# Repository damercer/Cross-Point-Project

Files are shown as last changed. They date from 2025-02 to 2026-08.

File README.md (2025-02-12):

# Cross Point Project
Software-Configured Breadboard Hardware Targeting Circuit Wiring Error Reduction in ECE Labs.
#
Abstract:
#
The hardware project aims to examine the effectiveness of software-configured wiring compared to traditional manual wiring of breadboards. While both methods use actual hardware, the software-configured approach automates the connections between components, thereby minimizing wiring errors and setup time. The intent is to investigate the impact of each approach on student comprehension, engagement, and error rates. By comparing these two approaches, the project seeks to determine which method better supports student engagement, educational outcomes and reduces frustration associated with complex circuit construction.
#
Introduction:
#
Hands-on experiential learning is a cornerstone of ECE education, typically relying on manual wiring of circuits on solderless breadboards. Using a traditional solderless breadboard as the means for building electronic circuit lab experiments requires the student, in addition to placing components, to manually insert wires to connect together the component pins according to a schematic diagram. These manual translation steps from schematic to hardware can lead to wiring errors in the experimental setup that can obscure circuit principles. While this manual wiring method offers valuable experience in physical component handling and troubleshooting, the extra time needed for debugging and correcting these errors leads to frustration and loss of precious lab time to investigate the circuit concept in question.

The goal is to evaluate the educational benefits and potential drawbacks of these software-configured hardware systems compared to traditional manual wiring. By doing so, it addresses the need for balancing hands-on skills with error minimization and conceptual understanding in electrical engineering education.
#
Analog switch matrix cross point experiment breadboard.
#
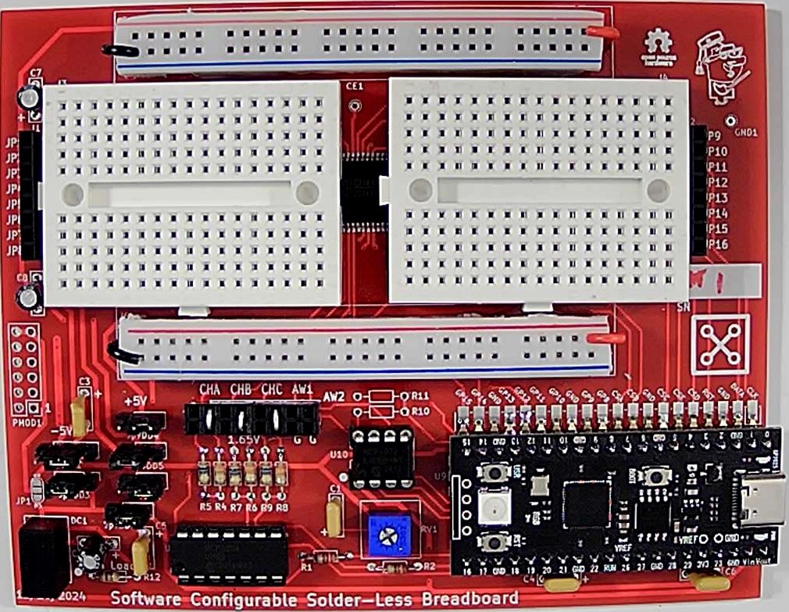
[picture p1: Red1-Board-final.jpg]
Screenshot Prototype PCB

Prototype PCB (Red version)
 
The idea is to computerize the wiring of the breadboard in an effort to reduce student frustration when building complex experiments. Using four analog 16X8 cross point switches wired together into two 32X8 cross points with a fifth switch matrix interconnecting the two smaller arrays into effectively a single 64X16 array.

This breadboard makes real, hardware connections between the 64 breadboard component pins on the board to the16 “jumper” nodes on the board via software commands, instead of needing to manually install jumper wires. The prototype PCB is shown, figure 1, which incorporates two mini 170 pin solderless breadboards, one for each of the 32X8 cross point arrays. There are a combined 68 total component pin locations across both mini breadboards with power distribution strips top and bottom. The two mini breadboards connect to the PCB through pogo pins and so they can be easily removed. It would then be possible to bolt on custom daughter PCBs with whatever components are needed for a given course already installed. Such as CMOS transistor arrays (CD4007) with even some pre-wired sub-circuits like current sources and OTAs.

The combined 64X16 cross point matrix board uses a total of 5 CH446DS 16X8 analog cross point ICs (from China) programed via a RP-2040 micro controller breakout board (Pi Pico or equivalent). Materials cost per board, in quantities of 10 or more, is less than $30 not including the assembly labor.

The board is powered from the Pi Pico USB connection. For powering the experiment circuits, male Pin Jumpers can be set for 0 and +3.3V, 0 and +5V or -5V and +5V power (or 0 and +10V) using an on board isolated 5V DC-DC generator.

LTspice is used to enter the schematic for the experiment. In addition to the standard library symbols a number of supporting schematic library files have been created. Schematic symbols for TO-92 transistors and resistors of various lead spacing are available in the LTspice files.

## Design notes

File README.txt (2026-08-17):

# Cross Point Project
Software-Configured Breadboard Hardware Targeting Circuit Wiring Error Reduction in ECE Labs.
#
Abstract:
#
The hardware project aims to examine the effectiveness of software-configured wiring compared to traditional manual wiring of breadboards. While both methods use actual hardware, the software-configured approach automates the connections between components, thereby minimizing wiring errors and setup time. The intent is to investigate the impact of each approach on student comprehension, engagement, and error rates. By comparing these two approaches, the project seeks to determine which method better supports student engagement, educational outcomes and reduces frustration associated with complex circuit construction.
#
Introduction:
#
Hands-on experiential learning is a cornerstone of ECE education, typically relying on manual wiring of circuits on solderless breadboards. Using a traditional solderless breadboard as the means for building electronic circuit lab experiments requires the student, in addition to placing components, to manually insert wires to connect together the component pins according to a schematic diagram. These manual translation steps from schematic to hardware can lead to wiring errors in the experimental setup that can obscure circuit principles. While this manual wiring method offers valuable experience in physical component handling and troubleshooting, the extra time needed for debugging and correcting these errors leads to frustration and loss of precious lab time to investigate the circuit concept in question.

The goal is to evaluate the educational benefits and potential drawbacks of these software-configured hardware systems compared to traditional manual wiring. By doing so, it addresses the need for balancing hands-on skills with error minimization and conceptual understanding in electrical engineering education.
#
Analog switch matrix cross point experiment breadboard.
#
Screenshot Prototype PCB
Production PCB (Red3 version, instructions for ordering boards can be found in PCB Projects folder)
 
The idea is to computerize the wiring of the breadboard in an effort to reduce student frustration when building complex experiments. Using four analog 16X8 cross point switches wired together into two 32X8 cross points with a fifth switch matrix interconnecting the two smaller arrays into effectively a single 64X16 array.

This breadboard makes real, hardware connections between the 64 breadboard component pins on the board to the 16 “jumper” nodes on the board via software commands, instead of needing to manually install jumper wires. The prototype PCB is shown, figure 1, which incorporates two mini 170 pin solderless breadboards, one for each of the 32X8 cross point arrays. There are a combined 68 total component pin locations across both mini breadboards with power distribution strips top and bottom. The two mini breadboards connect to the PCB through pogo pins and so they can be easily removed. It would then be possible to bolt on custom daughter PCBs with whatever components are needed for a given course already installed. Such as CMOS transistor arrays (CD4007) with even some pre-wired sub-circuits like current sources and OTAs.

The combined 64X16 cross point matrix board uses a total of 5 CH446DS 16X8 analog cross point ICs (from China) programed via a RP-2040 micro controller breakout board (Pi Pico or equivalent). Materials cost per board, in quantities of 10 or more, is less than $30 not including the assembly labor.

The board is powered from the Pi Pico USB connection. For powering the experiment circuits, Jumpers can be configured for 0 and +3.3V, 0 and +5V or -5V and +5V power using an on board isolated 5V DC-DC generator. Pi Pico microcontroller internal 12 bit ADC along with an external dual 12 bit DAC provide some level of data acquisition measurement capability for experiments.

LTspice is used to enter the schematic for the experiment. In addition to the standard library symbols a number of supporting schematic library files have been created. Schematic symbols for TO-92 transistors and resistors of various lead spacing are available in the LTspice files.

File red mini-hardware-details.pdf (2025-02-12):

## Red Mini Hardware Construction (revised 1/20/25):

Analog switch matrix cross point experiment breadboard.

The idea is to computerize the wiring of the breadboard in an effort to reduce student frustration when building complex experiments. Using four analog 16X8 cross point switches wired together into two 32X8 cross points with a fifth switch matrix interconnecting the two smaller arrays into effectively a single 64X16 array.

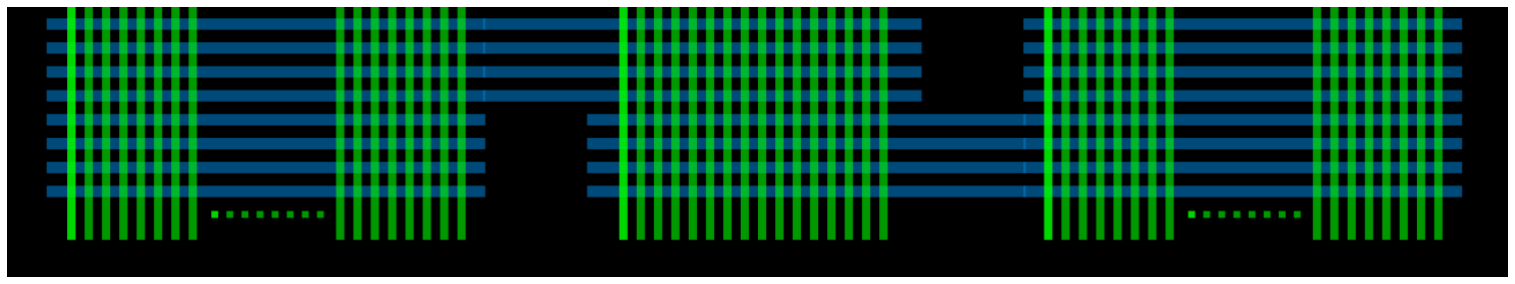
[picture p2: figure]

This breadboard makes real, hardware connections between the 64 breadboard component pins on the board to the16 “jumper” nodes on the board via software commands, instead of needing to manually install jumper wires. The prototype PCB is shown, figure 1, which incorporates two mini 170 pin solderless breadboards, one for each of the 32X8 cross point arrays. There are a combined 68 total component pin locations across both mini breadboards with power distribution strips top and bottom. The two mini breadboards connect to the PCB through pogo pins and so they can be easily removed. It would then be possible to bolt on custom daughter PCBs with whatever components are needed for a given course already installed. Such as CMOS transistor arrays (CD4007) with even some pre-wired sub-circuits like current sources and OTAs.

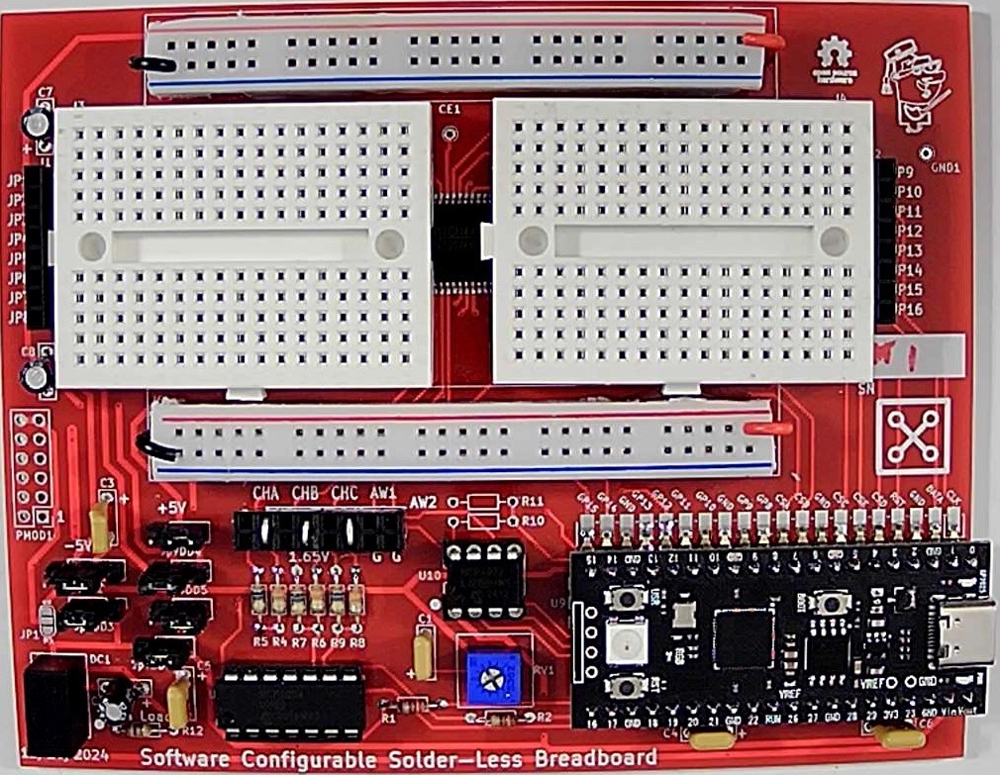
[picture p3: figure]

Figure 1, Prototype PCB.

The combined 64X16 cross point matrix board uses a total of 5 CH446DS [2] 16X8 analog cross point ICs (from China) programed via a RP-2040 micro controller breakout board (Pi Pico[3]
or equivalent).
Materials cost per board, in quantities of 10 or more, is less than $30 not including the assembly labor.

The board is powered from the Pi Pico USB connection. For powering the experiment circuits, male Pin Jumpers can be set for 0 and +3.3V, 0 and +5V or -5V and +5V power (or 0 and +10V) using an on board isolated 5V DC-DC generator.
LTspice[4]
is used to enter the schematic for the experiment. In addition to the standard library symbols a number of supporting schematic library files have been created, figure 2. Schematic symbols for TO-92 transistors and resistors of various lead spacing have been created. There are also example schematic symbols with the proper pin spacing for 8, 14 and 16 pin DIP packages. The standard library components can of course also be used.

The library schematics for the switch matrix connections contain 60 Ω resistors and 16 pF capacitors which model the analog switch. One end of a matrix switch will have the component pin net and the other end will have one of the 16 "jumper" nets (JP1-16).

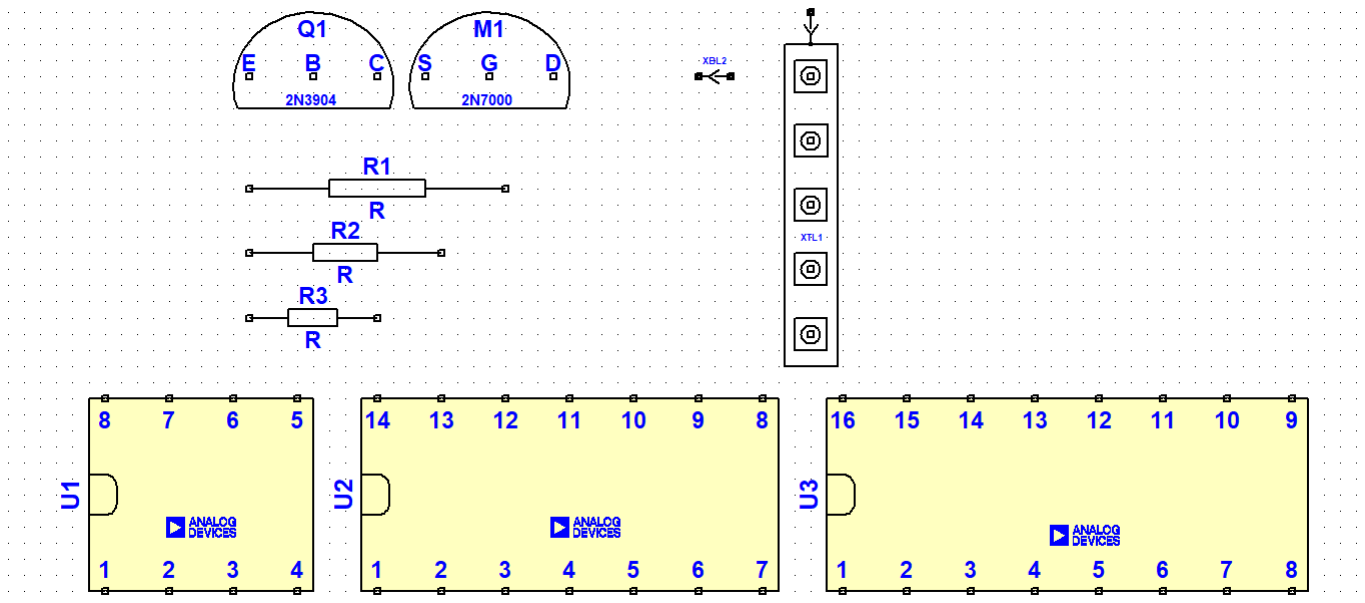
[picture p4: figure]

Figure 2, Schematic symbols.

A floor planning schematic template, figure 3, has been created to help the user figure out where to place the parts on the left and right side mini breadboards and then use the "jumpers" to wire them together. There is a schematic symbol for each breadboard column (the 5 pins shorted together). Each breadboard column has a specific name based on its location. Names are numbered from 1 to 17 starting with the top left section, TL1-17, then the bottom left section, BL1-17, then the top right section TR1-17, and finally the bottom right section, BR1-17.

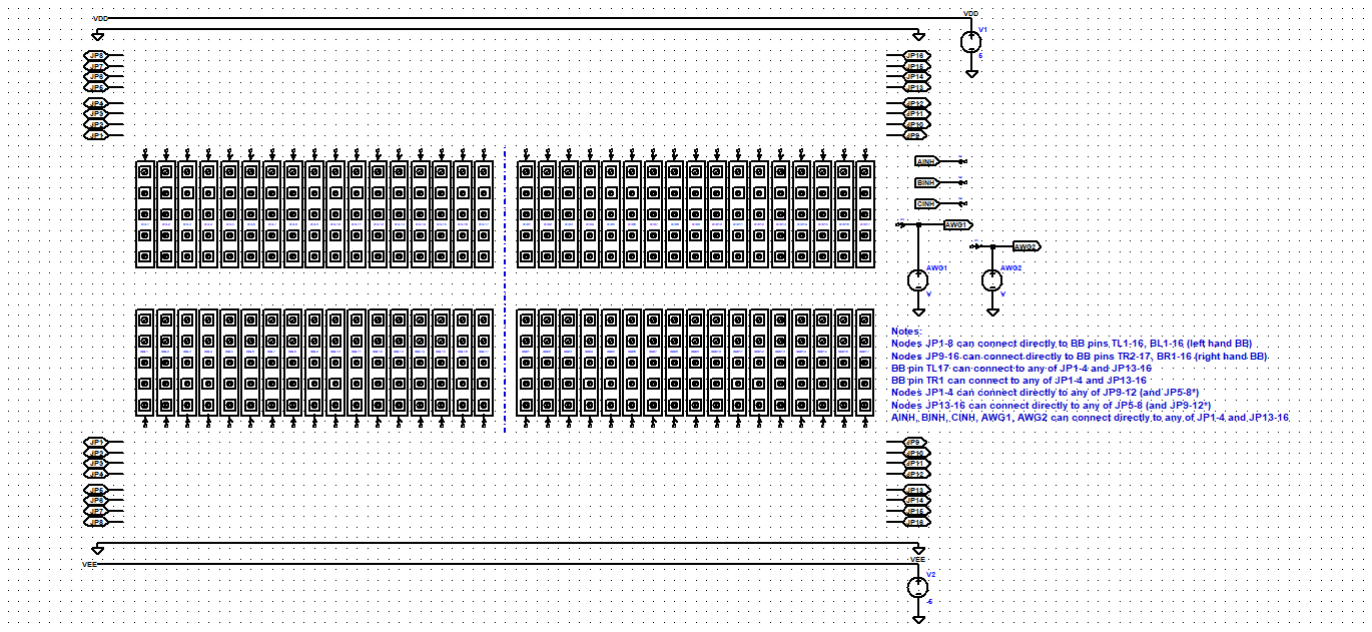
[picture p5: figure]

Figure 3, LTspice floor planner template schematic

In figure 4 we see an example circuit of a transistor level op-amp that has been floorplanned and interconnected with the JP jumper nets. Components can also be connected between a column pin and one of the top and bottom power and ground rails simply by a wire.

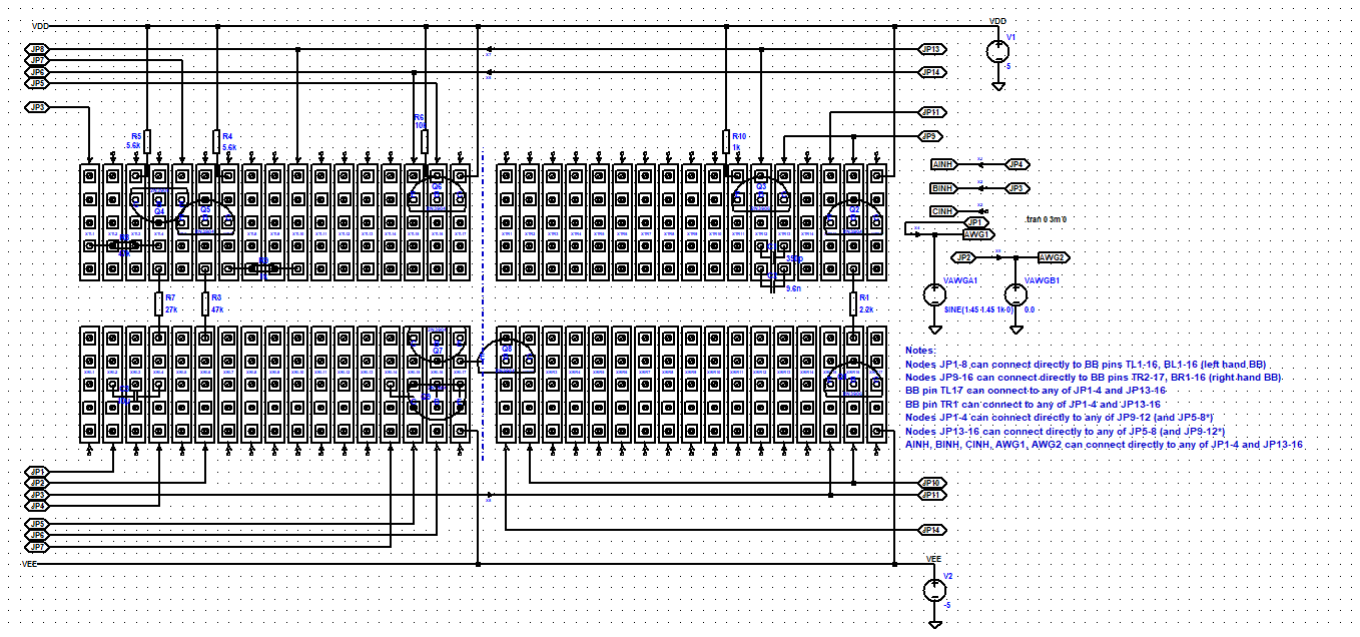
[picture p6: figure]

Figure 4, Example floor planned circuit

There is also a way to draw the circuit as a more conventional schematic, figure 5. The same op-amp circuit has been redrawn using standard symbols from the LTspice library with the addition of single switch interconnection symbols. The little pointy arrow symbols are placed in series with certain nets to indicate the component locations on the breadboard. These interconnection symbols are again named based on the BB holes (TL1-17, BL1-17, TR1-17, BR1-17) the parts are plugged into. This approach is easier to visualize the circuit as a schematic but perhaps harder to floor plan where to place the devices.

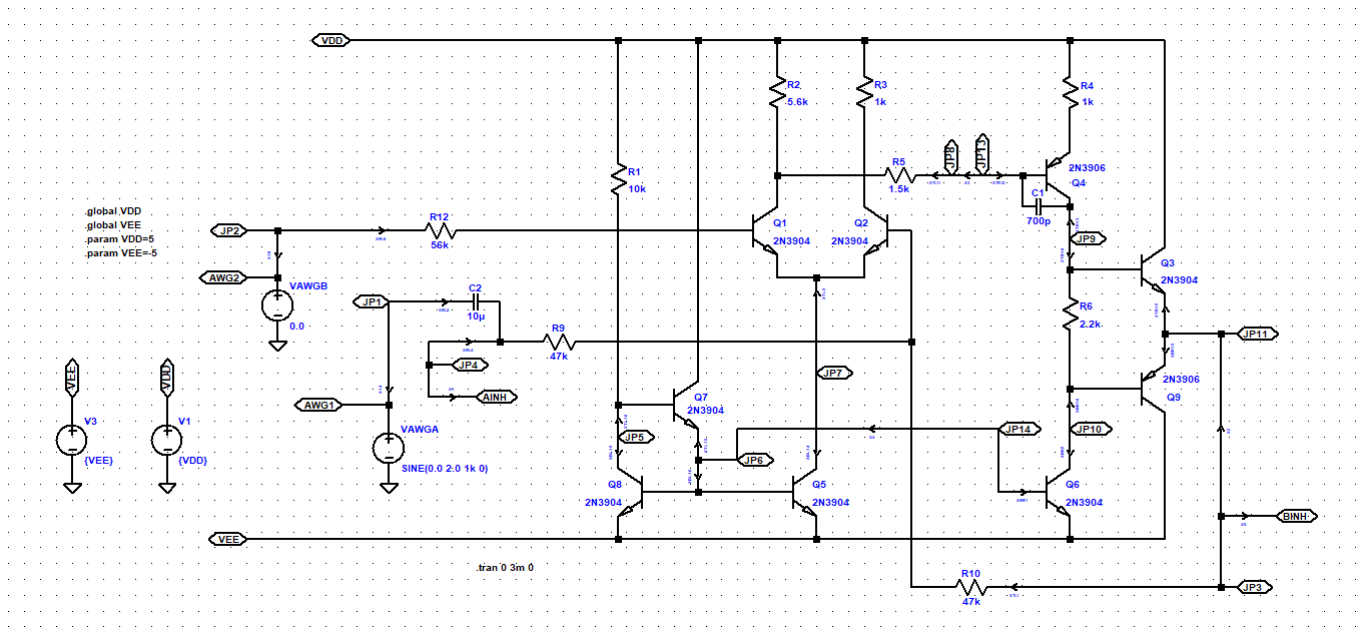
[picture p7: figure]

Figure 5, Conventional Schematic method

Correct simulation results insure that you have it all wired correctly before moving to the actual hardware.

A Python script looks through the saved LTspice .cir net list file looking for sub circuits starting with XX in their names. Then parses the connections based on the names (based on breadboard pin locations, TL1-17, BL1-17, TR1-17, BR1-17) and JP1-16 to send commands to the Pi Pico and on to the cross point switches. Everything else is ignored.

As long as you follow these rules when building the schematic the process is simple and mostly automatic. Programming the board is done through ALICE Universal[5]
using a hardware specific
interface configuration file for this cross point prototype including a way to turn on and off matrix switches manually as well.

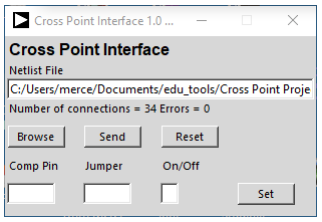
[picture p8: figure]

Cross Point Matrix control user interface The following are a few additional example circuits built using the breadboard.
The LTspice schematic in figure 6 was used to configure four CD4007 transistor arrays as a ring oscillator consisting of 11 CMOS inverter stages. It uses 56 of the 68 possible device pins and all 16 of the jumpers of the switch matrix. Manual jumper wires are used to connect each of the DIP (pins 7 and 14) ground and power pins to the power and ground rails on the board. All other connections are programed by the netlist.

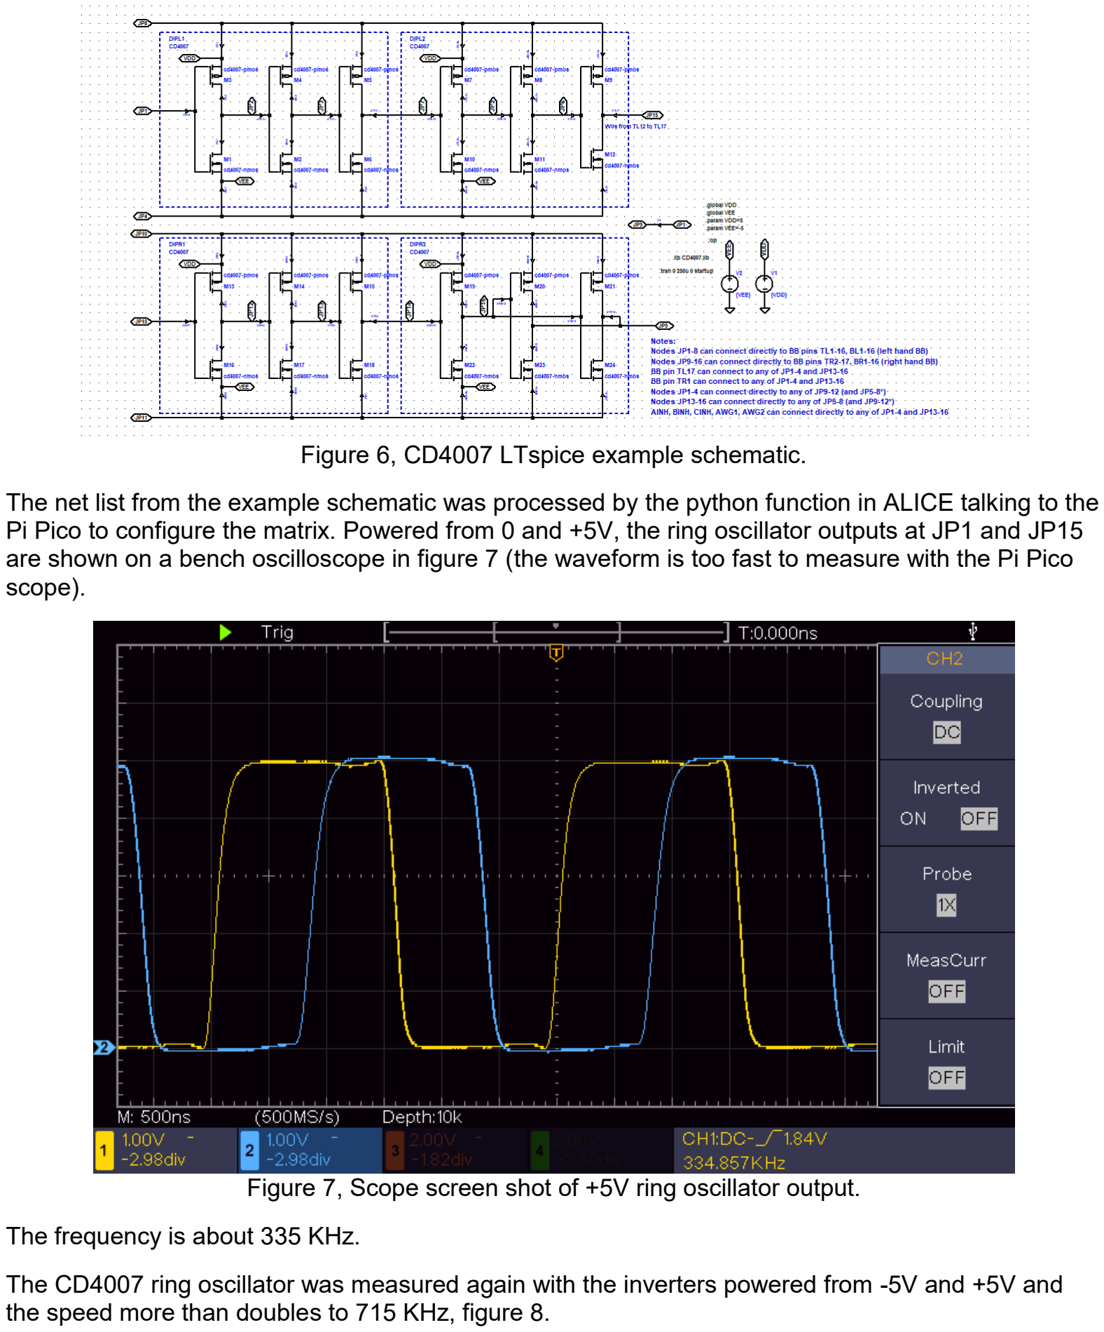
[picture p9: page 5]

Figure 6, CD4007 LTspice example schematic.

The net list from the example schematic was processed by the python function in ALICE talking to the Pi Pico to configure the matrix. Powered from 0 and +5V, the ring oscillator outputs at JP1 and JP15 are shown on a bench oscilloscope in figure 7 (the waveform is too fast to measure with the Pi Pico scope).

Figure 7, Scope screen shot of +5V ring oscillator output.

The frequency is about 335 KHz.

The CD4007 ring oscillator was measured again with the inverters powered from -5V and +5V and the speed more than doubles to 715 KHz, figure 8.

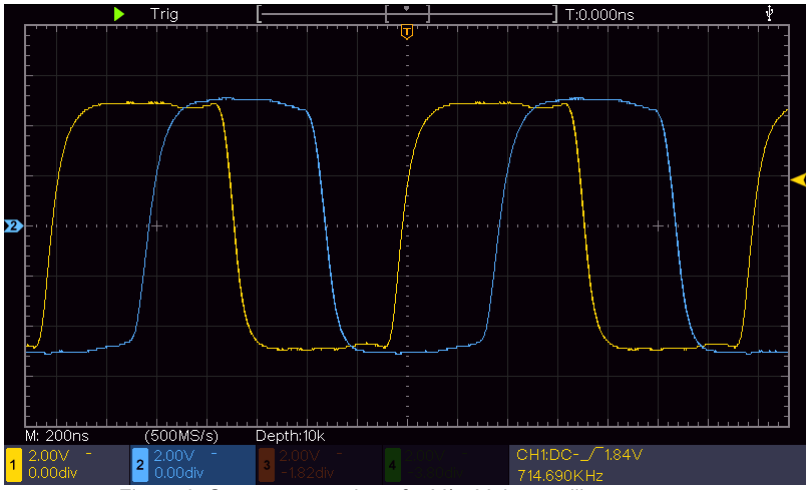
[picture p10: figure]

Figure 8, Scope screen shot of -5V/+5V ring oscillator output.

A Schmitt trigger relaxation oscillator can be constructed from the CD4007 CMOS transistor level inverters, figure 9. The Schmitt trigger is made by rearranging the connections and adding resistor R1 and Capacitor C1 to set the frequency. The M1,3 and M7,10 inverters are stronger than the other 4 inverters because their sources are connected directly to VDD and VEE rather than through the 60 Ω switch resistances. A “strong” inverter and a “weak” inverter are connected as a latch. This latch action determines the high and low threshold of the Schmitt trigger.

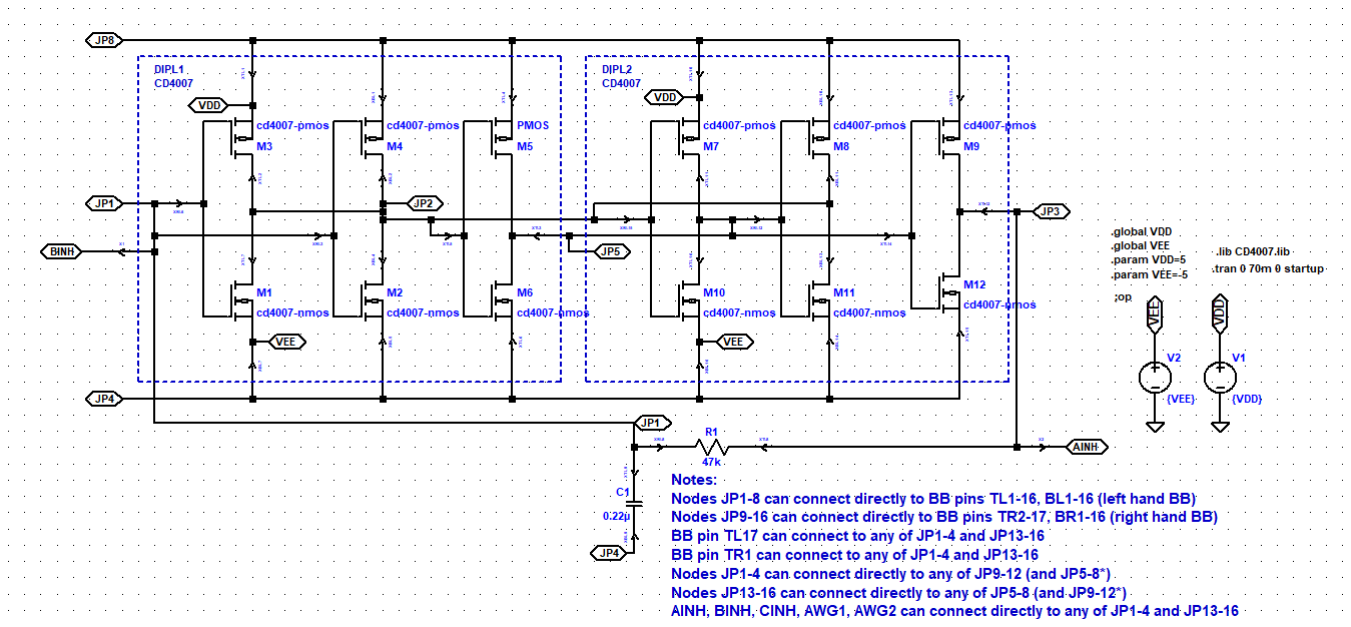
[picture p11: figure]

Figure 9, CMOS inverter relaxation oscillator.

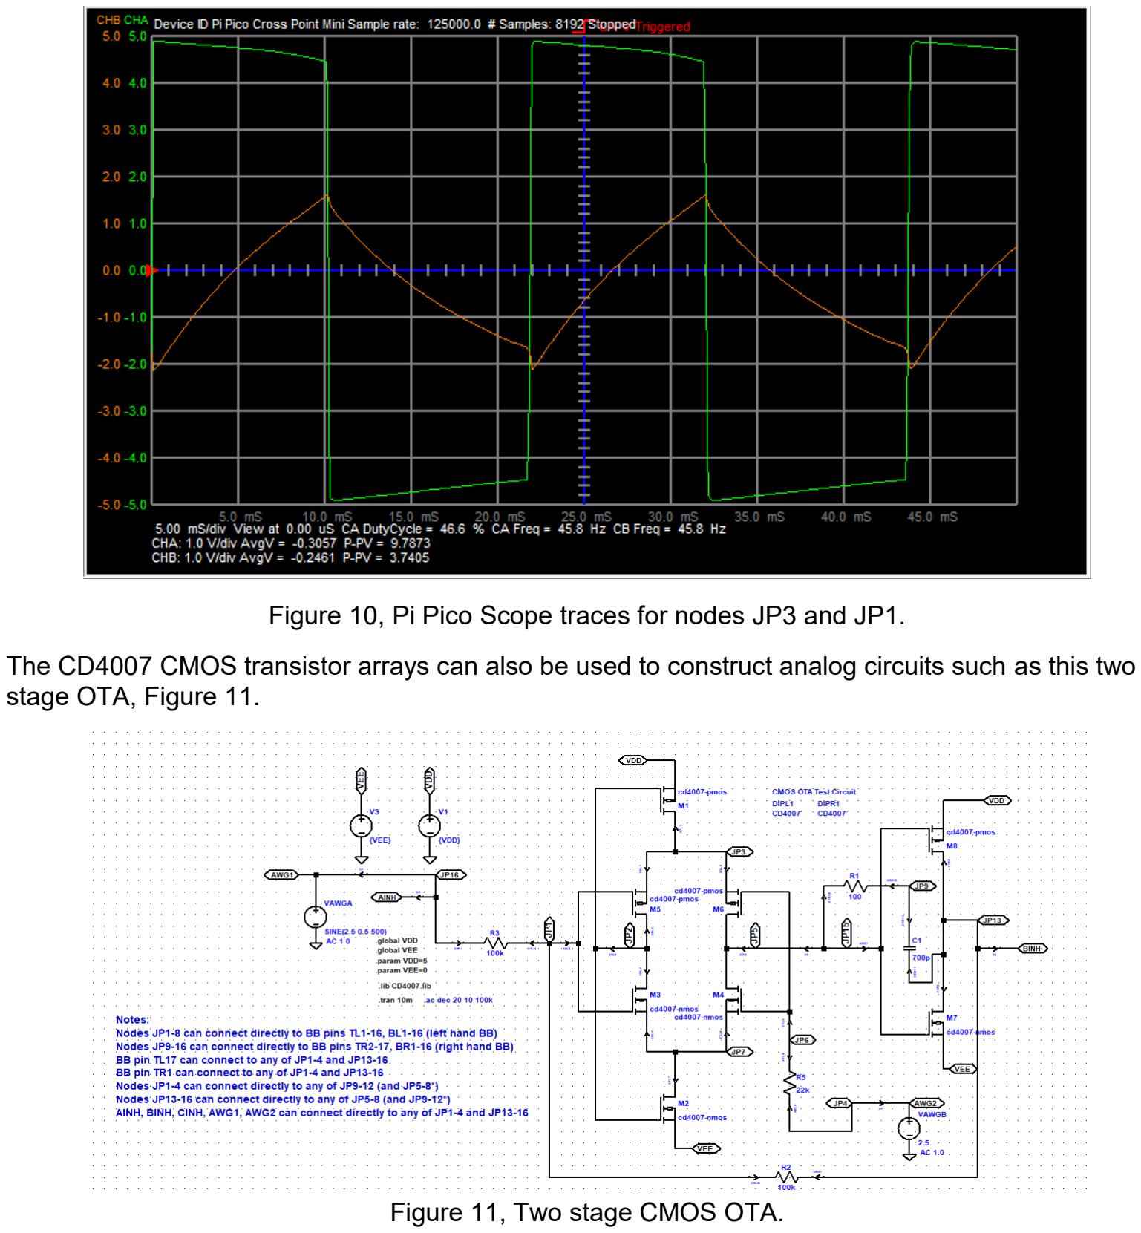
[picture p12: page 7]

Figure 10, Pi Pico Scope traces for nodes JP3 and JP1.

The CD4007 CMOS transistor arrays can also be used to construct analog circuits such as this two stage OTA, Figure 11.

Figure 11, Two stage CMOS OTA.

References:

[1] Jumperless breadboard product, https://www.tindie.com/products/architeuthisflux/jumperless/ , https://github.com/Architeuthis-Flux/Jumperless
[2] CH446DS1 datasheet, https://www.wch-ic.com/downloads/CH446DS1_PDF.html
[3] Pi Pico, https://www.digikey.com/en/products/detail/raspberry-pi/SC0915/13684020?utm_adgroup=&gad_source=1 (https://www.digikey.com/en/products/detail/raspberry-pi/SC0915/13684020?utm_adgroup=&gad_source=1)
[4] LTspice, https://www.analog.com/en/resources/design-tools-and-calculators/ltspice-simulator.html
[5] ALICE Universal, https://github.com/damercer/Universal-ALICE

Construction order of operations:

The order of assembly operations is first to install all the components that are soldered using hot air.

The first things requiring solder paste and hot air to install on the board are the pogo pins. Add a small dollop of solder paste in each pogo pin hole. Then insert a pogo pin (spring end up) in each hole. Using hot air reflow the solder paste until each pin flows down level into its hole.

The second things to install are the CH446DS quad flat pack ICs. Apply a small amount of solder paste along the four sides of the footprint. Using a conventional soldering iron melt the solder paste and “tin” the PCB lands with small mounds of fresh solder. The correct amount of solder will generally be left behind on each pin as the soldering iron is slowly dragged across the PCB.

Note the small white dot on the PCB near the lower left of each footprint on the PCB. This needs to be aligned with the dot on the IC package. It is a good idea to have all five of the packages properly aligned / orientated before hand. Mount the ICs one at a time. Using the hot air heat each IC footprint until the solder starts to melt. Using tweezers pick up the IC package, remembering to keep the proper orientation with the white dot, and place it on the melted solder. The IC should self-align and float on the melted solder by surface tension. You may need to nudge the IC slightly with the tweezers depending on how close it was to the proper position when you placed it. Remove the hot air as soon as it looks aligned properly to not over heat the IC.

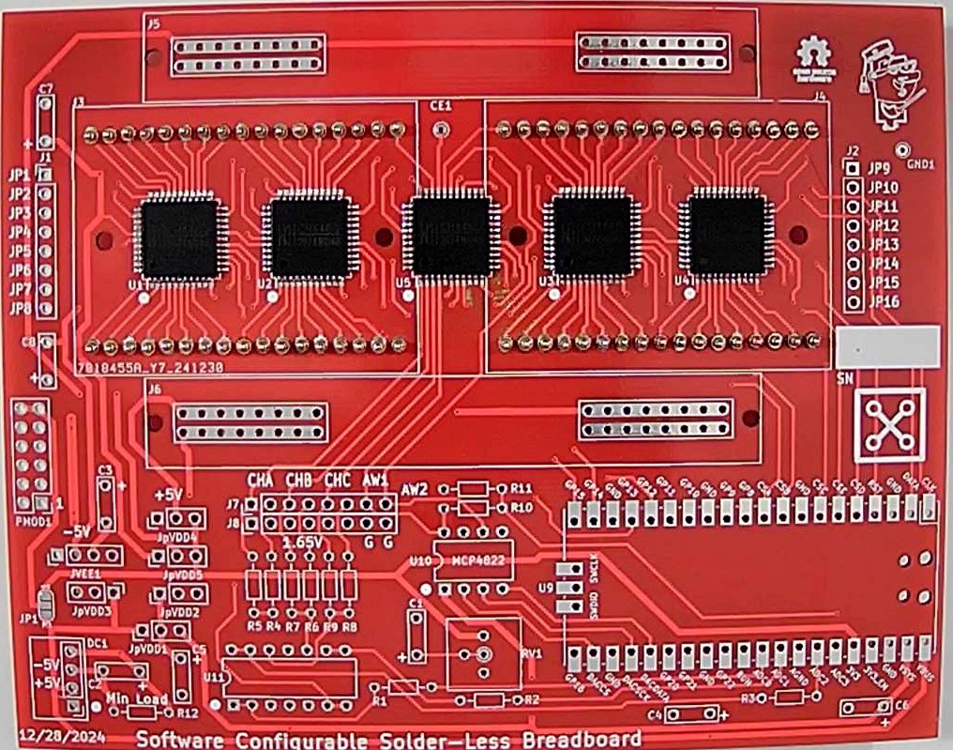
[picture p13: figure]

When installing the rest of the components which are through hole, it is best to start with the shortest devices (closest to the surface of the board). These would be the resistors. Then move to the next tallest etc. A small strip of masking tape can be used to temporarily hold the components tight to the board when you flip the board over to solder the leads from the bottom.

Additional Notes:

Software Configurable Solderless Breadboard Connections

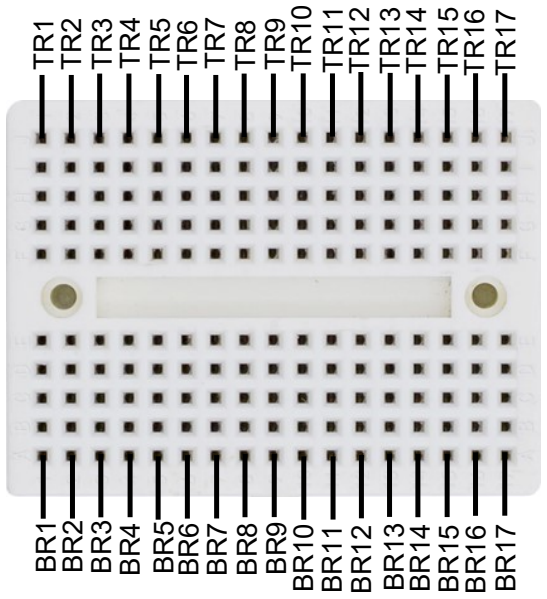
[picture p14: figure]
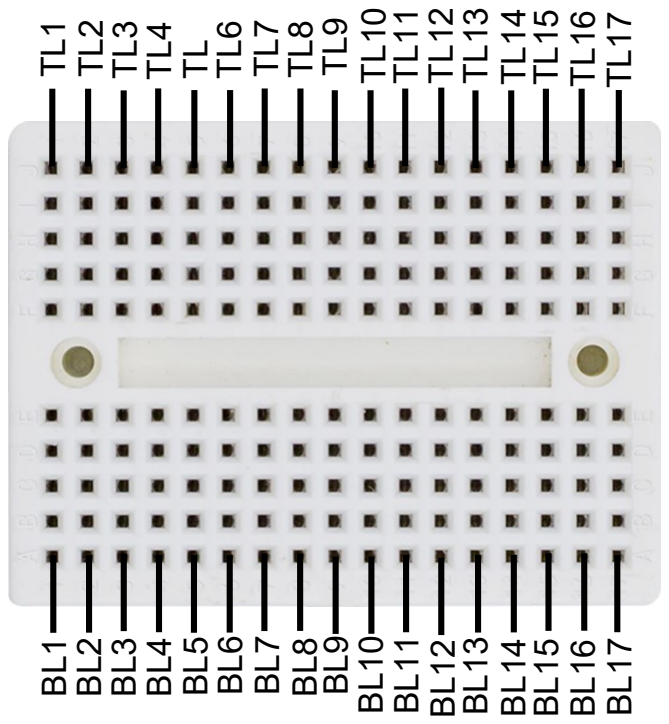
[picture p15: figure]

Mini Solderless Breadboard Pin Names (Red)

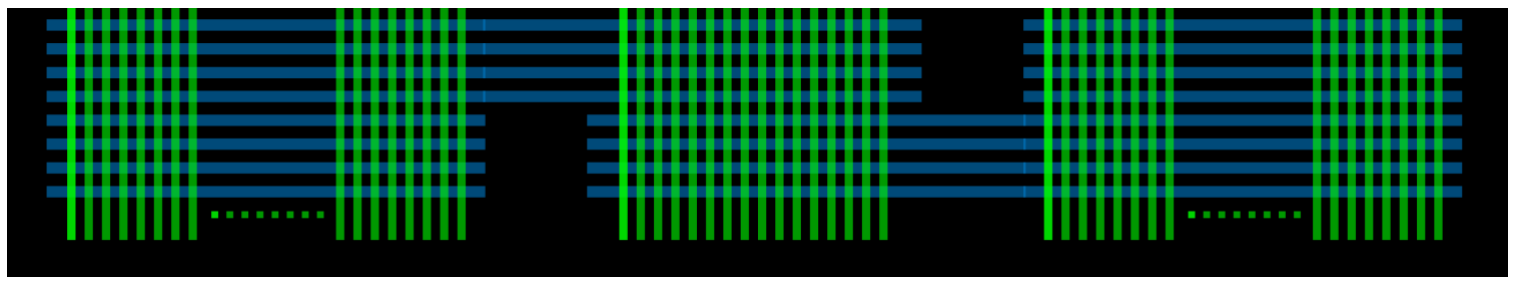
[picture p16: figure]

Notes:

Switch Nodes JP1-8 can connect directly to BB pins TL1-16, BL1-16 (left hand BB) Switch Nodes JP9-16 can connect directly to BB pins TR2-17, BR1-16 (right hand BB) BB pin TL17 can connect to any of JP1-4 and JP13-16
BB pin TR1 can connect to any of JP1-4 and JP13-16
Switch Nodes JP1-4 can connect directly to any of JP9-12 (and JP5-8*)
Switch Nodes JP13-16 can connect directly to any of JP5-8 (and JP9-12*)
AINH, BINH, CINH, AWG1, AWG2 can connect directly to any of JP1-4 and JP13-16

BL17 and BR17 normally default as open circuit but can be optionally connected to -5 V power rail using solder jumpers marked JP3 and JP4 on the underside of the board. TL1 TL2 BL1 BL2 TL3 BL3 TL

BL5

TL6

TL7

TL9

TL10
TL11

BL6
BL7

BL9

BL10
BL11

TL13
TL14
TL15

BL13
BL14
BL15

TR2
TR3

TR4
TR6

TR7
TR8

TR10
TR11
TR12

TR14

TR15
TR16

BR2
BR3
BR4
BR6

BR7

BR8
BR10
BR11
BR12

BR14
BR15
BR16

BR5
BR13

Power Rail Jumper Configuration:

The standard Pi Pico pinout has two possible positive voltages supplied from the USB port. The VBUS pin is directly connected to the USB connector +5V. The VSYS pin has a diode in series with USB connector +5V. The board has 6 jumper locations that are used to configure and distribute voltages on the board. The analog switches are powered from the VDD1 positive voltage trace (+5V) and VEE1 negative voltage trace (-5V). How VDD1 and VEE1 are configured is determined by how the jumpers are shorted.

Jumper jpVDD1 (see picture below) is a three pin jumper where the center pin can be shorted to either the left or right pin. Installing a short between center and left pin connects VDD1 to VBUS. Installing a short between center and right pin connects VDD1 to VSYS.

The on board isolated DC/DC converter is powered directly from the VBUS pin. The isolated 5V output can be connected two ways using Jumpers jpVDD2 and jpVDD3. The positive output terminal on the center pin of jpVDD2 can be connected to ground by shoring it to the right pin (GND) or the VDD1 trace by shorting it to the left pin. When the positive output terminal is connected to ground the output negative terminal becomes -5V with respect to ground and is connected to the center pin of jumper jpVDD3. This -5V can be connected to VEE1 by shorting the center pin to the left pin.

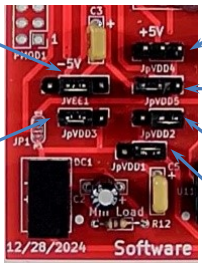
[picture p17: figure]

The board has four power distribution rails. Two on the top and two on the bottom. The lower of the two top power rails is always connected to GND. The pins of jumper jpVDD5 determine what voltage supplies the upper half of the top rail. The center pin of jpVDD5 is connected to the upper half of the top rail. Shorting the left pin to the center connects to VDD1 and shorting the right pin to the center connects to the +3.3V supplied by the Pi Pico on board LDO.

Four pin jumper jVEE1 determines the voltage supplied to the lower of the two bottom power rails. Shorting the two center pins connects it to the VEE1 (generally -5V). Three pin jumper jpVDD4 determines the voltage supplied to the upper of the two bottom power rails. Shorting the left pin to center pin connects to GND. Shorting the right pin to center pin connects to +3.3V.

jpVDD1
Right to connect to VSYS
Left to connect to VBUS

jpVDD2
Right to connect to GND

jpVDD3
Left to connect to GND

jVEE1
Short center two pins

jpVDD4
Left to connect to GND
Right to connect to +3.3V
jpVDD5
Left to connect to VDD1
Right to connect to +3.3V

Pi Pico Black with 4 MB flash and Type C USB modifications:

This Black clone of the Pi Pico has some interesting differences between it and the standard (Green) Pi Pico.

First is, it provides access to the ADC3 mux input.

The second difference is how Power pins (40 and 39 lower right) are arranged with respect to the power supplied from the USB connector. Note the two pictures below. A short needs to be added to the Black boards.

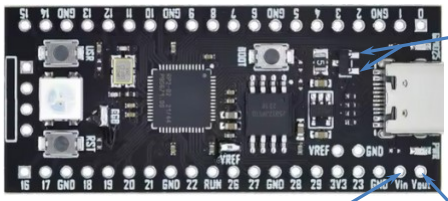
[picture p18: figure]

Solder a short across
these two pins.

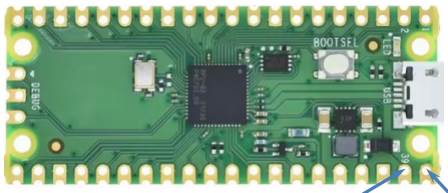
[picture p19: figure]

Full USB voltage appears
on this Pin.

Normally this pin is use to apply external power onto board. With short added full USB voltage now comes out on this Pin.

USB voltage less one
diode drop appears on
this Pin.

USB voltage less one
diode drop appears on
this Pin rather than the
full USB voltage.

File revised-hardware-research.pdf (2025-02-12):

## Hardware Research (revised 1/18/25):

Software-Configured Breadboard Hardware Targeting Circuit Wiring Error Reduction in ECE Labs.

Abstract:

The hardware project aims to examine the effectiveness of software-configured wiring compared to traditional manual wiring of breadboards. While both methods use actual hardware, the software-configured approach automates the connections between components, thereby minimizing wiring errors and setup time. The intent is to investigate the impact of each approach on student comprehension, engagement, and error rates. By comparing these two approaches, the project seeks to determine which method better supports student engagement, educational outcomes and reduces frustration associated with complex circuit construction.

Introduction:

Hands-on experiential learning is a cornerstone of ECE education, typically relying on manual wiring of circuits on solderless breadboards. Using a traditional solderless breadboard as the means for building electronic circuit lab experiments requires the student, in addition to placing components, to manually insert wires to connect together the component pins according to a schematic diagram. These manual translation steps from schematic to hardware can lead to wiring errors in the experimental setup that can obscure circuit principles. While this manual wiring method offers valuable experience in physical component handling and troubleshooting, the extra time needed for debugging and correcting these errors leads to frustration and loss of precious lab time to investigate the circuit concept in question.

Recently, commercially available software-configurable bread boarding platforms have emerged[1], allowing users to build real circuits with automated wiring based on computer software input, thus retaining the tactile experience while minimizing connection errors. The intent is not to compare such commercial devices since the development of the proposed lower cost system (See more details in Appendix below) is progressing well.

As additional background, one approach that has been used to reduce wiring mistakes is to build pre-wired printed circuit experiment boards[2]. However, this approach has limited configurability and component flexibility to explore multiple circuit configurations. In addition pre-wired printed circuit boards do not offer the same level of experience in physical component handling, troubleshooting and debugging.

The goal is to evaluate the educational benefits and potential drawbacks of these software-configured hardware systems compared to traditional manual wiring. By doing so, it addresses the need for balancing hands-on skills with error minimization and conceptual understanding in electrical engineering education.

High Level Development Plan:

The goal of this project is to develop and build a “smart” software defined or configurable breadboard system (SCB). The proposed project leverages the results of the prototype hardware outlined in the appendix below now under investigation.

- Construct software configurable breadboard hardware for pilot evaluation.
- Develop / Adapt pilot course materials based on existing solderless breadboard labs that motivate the design and demonstrate its capabilities. Initial focus will be on basic functionality.
- Explore and develop build on demand / build to order supply chain(s) for the hardware. Exploring ways to cost effectively obtain such hardware may actually be a more important broadly impactful aspect of this project.

Potential Implications:

The results of this study could have significant implications for the design of electronics lab curricula. If software-configurable hardware systems are found to be more effective in reducing errors without compromising learning, they could be integrated into introductory courses to provide a balanced learning experience. Conversely, if manual wiring proves essential for certain skill development, educators may consider using a hybrid approach in some courses, incorporating both methods based on learning objectives.

Overall Plan for the Budget (to be determined by principal researchers):

-The base budget for the project is:

- Materials cost, $2000 (approx. for 24 boards)
- Faculty Hours?
- Staff support Hours?
- Student Hours?

Appendix:

Analog switch matrix cross point experiment breadboard.

The idea is to computerize the wiring of the breadboard in an effort to reduce student frustration when building complex experiments. Using four analog 16X8 cross point switches wired together into two 32X8 cross points with a fifth switch matrix interconnecting the two smaller arrays into effectively a single 64X16 array. This breadboard makes real, hardware connections between the 64 component pins on the board to the16 “jumper” nodes on the board via software commands, instead of needing to manually install jumper wires. The prototype PCB is shown, figure 1, which incorporates two mini 170 pin solderless breadboards, one for each of the 32X8 cross point arrays. There are a combined 68 total component pin locations across both mini breadboards with power distribution strips top and bottom. The two mini breadboards connect to the PCB through pogo pins and so they can be easily removed. It would then be possible to bolt on custom daughter PCBs with whatever components are needed for a given course already installed. Such as CMOS transistor arrays (CD4007) with even some pre-wired sub-circuits like current sources and OTAs.


Figure 1, Prototype PCB.
The combined 64X16 cross point matrix board uses a total of 5 CH446DS [2] 16X8 analog cross point ICs (from China) programed via a RP-2040 micro controller breakout board (Pi Pico[3]
or equivalent).
Materials cost per board, in quantities of 10 or more, is less than $30 not including the assembly labor.

The board is powered from the Pi Pico USB connection. Male Pin Jumpers for powering the experiment can be set for 0 and +3.3V, 0 and +5V or -5V and +5V power (or 0 and +10V) using an on board isolated 5V DC-DC generator.

LTspice[4]
is used to enter the schematic for the experiment. In addition to the standard library symbols a number of supporting schematic library files have been created, figure 2. Schematic symbols for TO-92 transistors and resistors of various lead spacing have been created. There are also example schematic symbols with the proper pin spacing for 8, 14 and 16 pin DIP packages. The standard library components can of course also be used.

The library schematics for the switch matrix connections contain 60 Ω resistors and 16 pF capacitors which model the analog switch. One end of a matrix switch will have the component pin net and the other end will have one of the 16 "jumper" nets (JP1-16).

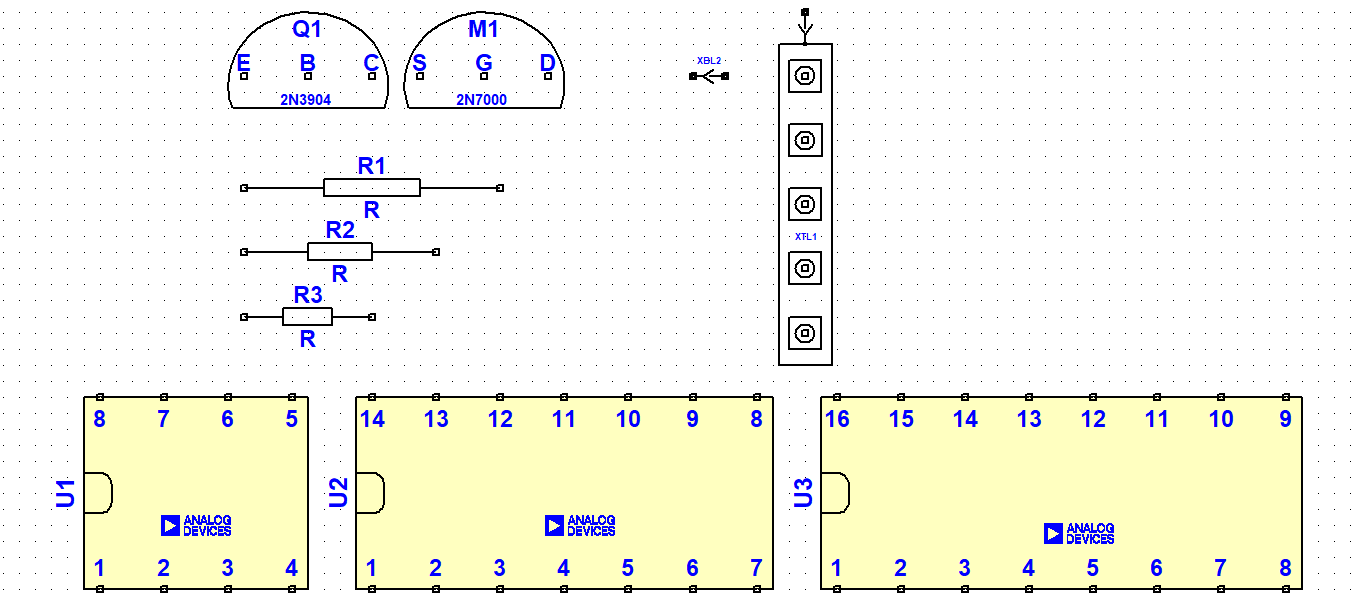
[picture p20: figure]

Figure 2, Schematic symbols.

A floor planning schematic template, figure 3, has been created to help the user figure out where to place the parts on the left and right side mini breadboards and then use the "jumpers" to wire them together. There is a schematic symbol for each breadboard column (the 5 pins shorted together). Each breadboard column has a specific name based on its location. Names are numbered from 1 to 17 starting with the top left section, TL1-17, then the bottom left section, BL1-17, then the top right section TR1-17, and finally the bottom right section, BR1-17.


Figure 3, LTspice floor planner template schematic

In figure 4 we see an example circuit of a transistor level op-amp that has been floorplanned and interconnected with the JP jumper nets. Components can also be connected between a column pin and one of the top and bottom power and ground rails simply by a wire.


Figure 4, Example floor planned circuit

There is also a way to draw the circuit as a more conventional schematic, figure 5. The same op-amp circuit has been redrawn using standard symbols from the LTspice library with the addition of single switch interconnection symbols. The little pointy arrow symbols are placed in series with certain nets to indicate the component locations on the breadboard. These interconnection symbols are again named based on the BB holes (TL1-17, BL1-17, TR1-17, BR1-17) the parts are plugged into. This approach is easier to visualize the circuit as a schematic but perhaps harder to floor plan where to place the devices.

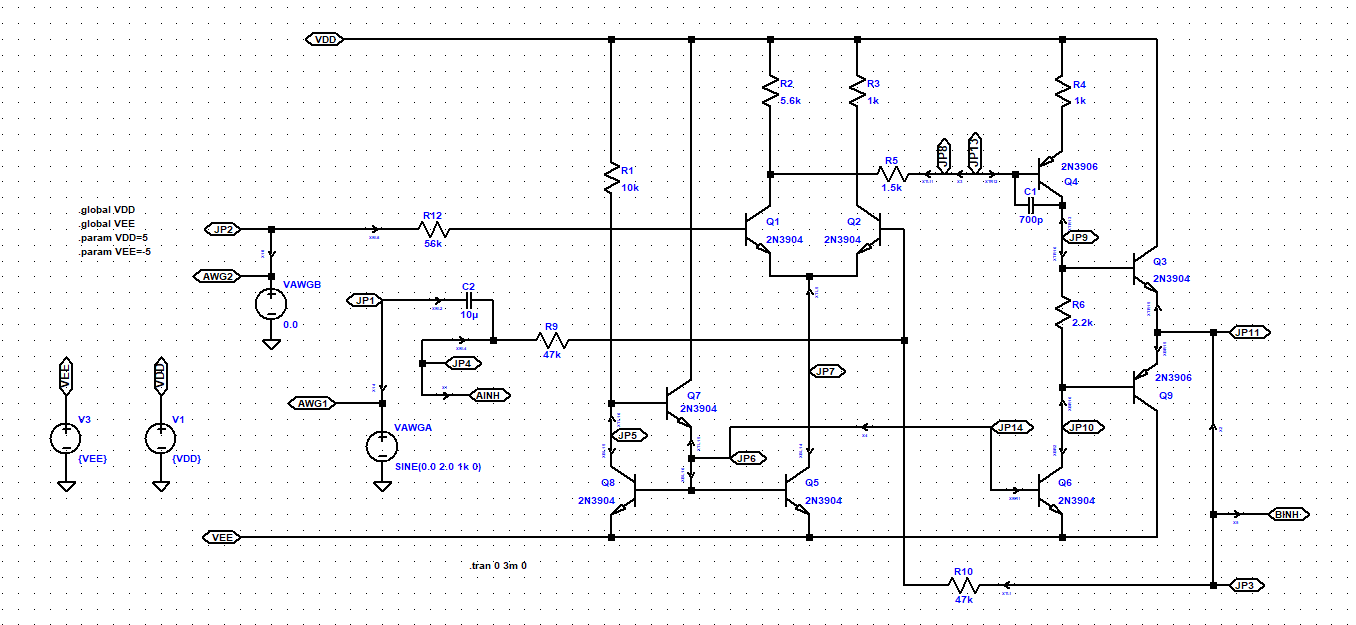
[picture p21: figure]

Figure 5, Conventional Schematic method

Correct simulation results insure that you have it all wired correctly before moving to the actual hardware.

A Python script looks through the saved LTspice .cir net list file looking for sub circuits starting with XX in their names. Then parses the connections based on the names (based on breadboard pin locations, TL1-17, BL1-17, TR1-17, BR1-17) and JP1-16 to send commands to the Pi Pico and on to the cross point switches. Everything else is ignored.

As long as you follow these rules when building the schematic the process is simple and mostly automatic. Programming the board is done through ALICE Universal[5]
using a hardware specific
interface configuration file for this cross point prototype including a way to turn on and off matrix switches manually as well.

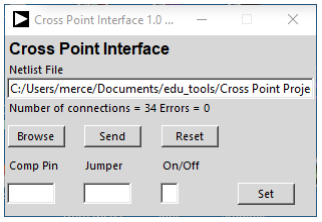
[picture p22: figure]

Cross Point Matrix control user interface The following are a few additional example circuits built using the breadboard.
The LTspice schematic in figure 6 was used to configure four CD4007 transistor arrays as a ring oscillator consisting of 11 CMOS inverter stages. It uses 56 of the 68 possible device pins and all 16 of the jumpers of the switch matrix. Manual jumper wires are used to connect each of the DIP (pins 7 and 14) ground and power pins to the power and ground rails on the board. All other connections are programed by the netlist.

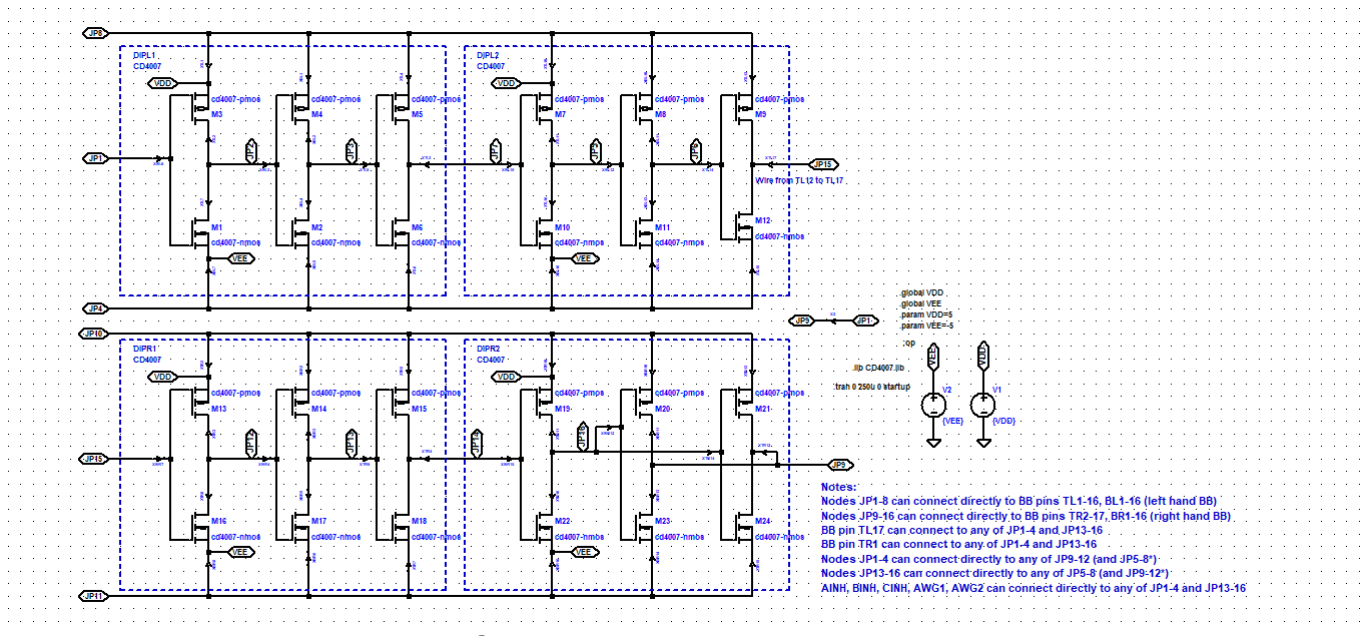
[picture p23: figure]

Figure 6, CD4007 LTspice example schematic.

The net list from the example schematic was processed by the python function in ALICE talking to the Pi Pico to configure the matrix. Powered from 0 and +5V, the ring oscillator outputs at JP1 and JP15 are shown on a bench oscilloscope in figure 7 (the waveform is too fast to measure with the Pi Pico scope).

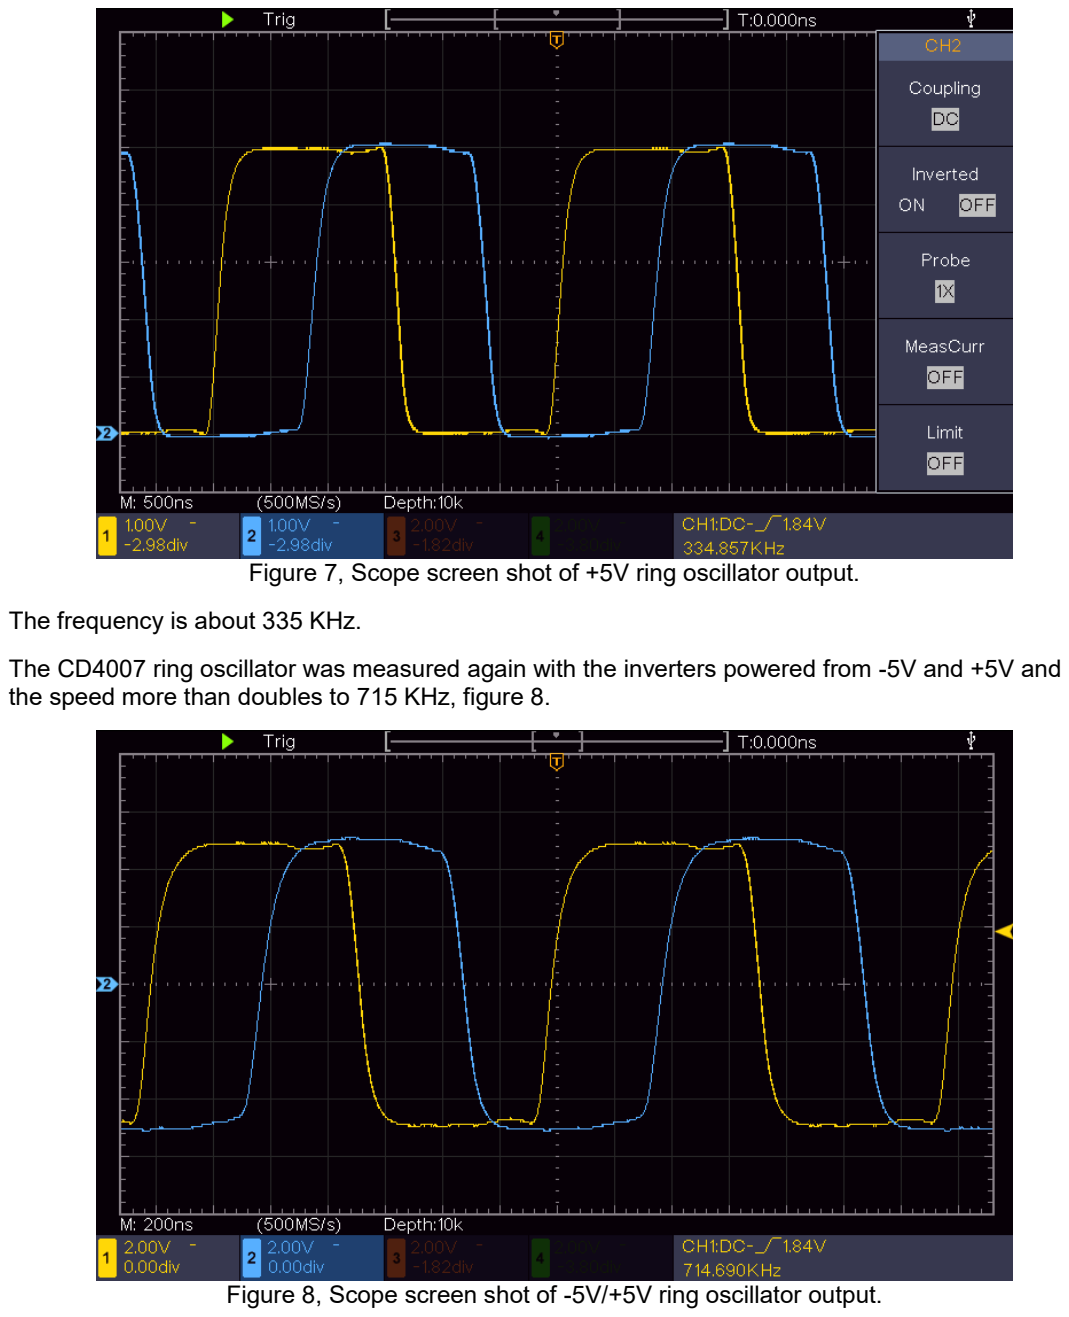
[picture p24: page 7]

Figure 7, Scope screen shot of +5V ring oscillator output.

The frequency is about 335 KHz.

The CD4007 ring oscillator was measured again with the inverters powered from -5V and +5V and the speed more than doubles to 715 KHz, figure 8.

Figure 8, Scope screen shot of -5V/+5V ring oscillator output.

A Schmitt trigger relaxation oscillator can be constructed from the CD4007 CMOS transistor level inverters, figure 9. The Schmitt trigger is made by rearranging the connections and adding resistor R1 and Capacitor C1 to set the frequency. The M1,3 and M7,10 inverters are stronger than the other 4 inverters because their sources are connected directly to VDD and VEE rather than through the 60 Ω switch resistances. A “strong” inverter and a “weak” inverter are connected as a latch. This latch action determines the high and low threshold of the Schmitt trigger.

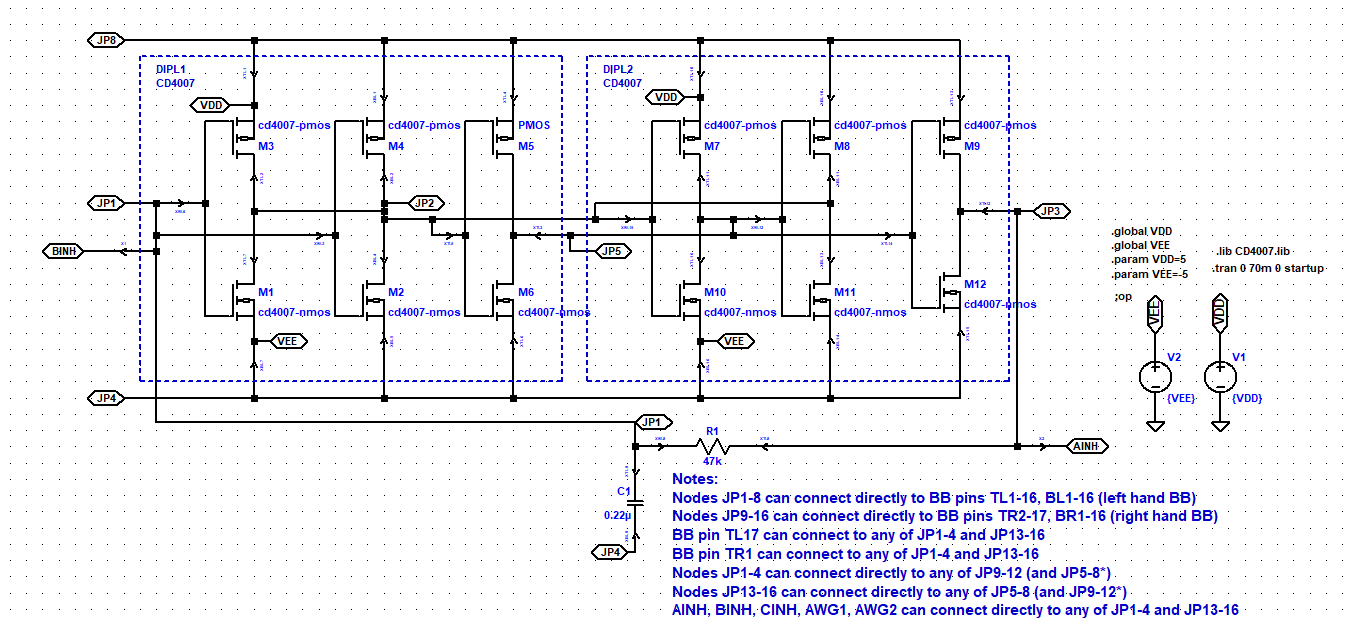
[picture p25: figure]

Figure 9, CMOS inverter relaxation oscillator.


Figure 10, Pi Pico Scope traces for nodes JP3 and JP1.

The CD4007 CMOS transistor arrays can also be used to construct analog circuits such as this two stage OTA, Figure 11.


Figure 11, Two stage CMOS OTA.

References:

[1] Jumperless breadboard product, https://www.tindie.com/products/architeuthisflux/jumperless/ , https://github.com/Architeuthis-Flux/Jumperless
[2] CH446DS1 datasheet, https://www.wch-ic.com/downloads/CH446DS1_PDF.html
[3] Pi Pico, https://www.digikey.com/en/products/detail/raspberry-pi/SC0915/13684020?utm_adgroup=&gad_source=1 (https://www.digikey.com/en/products/detail/raspberry-pi/SC0915/13684020?utm_adgroup=&gad_source=1)
[4] LTspice, https://www.analog.com/en/resources/design-tools-and-calculators/ltspice-simulator.html
[5] ALICE Universal, https://github.com/damercer/Universal-ALICE

Additional Notes:

Software Configurable Solderless Breadboard Connections


Mini Solderless Breadboard Pin Names (Red)

Notes:

Switch Nodes JP1-8 can connect directly to BB pins TL1-16, BL1-16 (left hand BB) Switch Nodes JP9-16 can connect directly to BB pins TR2-17, BR1-16 (right hand BB) BB pin TL17 can connect to any of JP1-4 and JP13-16
BB pin TR1 can connect to any of JP1-4 and JP13-16
Switch Nodes JP1-4 can connect directly to any of JP9-12 (and JP5-8*)
Switch Nodes JP13-16 can connect directly to any of JP5-8 (and JP9-12*)
AINH, BINH, CINH, AWG1, AWG2 can connect directly to any of JP1-4 and JP13-16

BL17 and BR17 normally default as open circuit but can be optionally connected to -5 V power rail using solder jumpers marked JP3 and JP4 on the underside of the board.

Power Rail Jumper Configuration:

The standard Pi Pico pinout has two possible positive voltages supplied from the USB port. The VBUS pin is directly connected to the USB connector +5V. The VSYS pin has a diode in series with USB connector +5V. The board has 6 jumper locations that are used to configure and distribute voltages on the board. The analog switches are powered from the VDD1 positive voltage trace (+5V) and VEE1 negative voltage trace (-5V). How VDD1 and VEE1 are configured is determined by how

# the jumpers are shorted. TL1 TL2 BL1 BL2 TL3 BL3 TL

BL5

TL6

TL7

TL9

TL10
TL11

BL6
BL7

BL9

BL10
BL11

TL13
TL14
TL15

BL13
BL14
BL15

TR2
TR3

TR4
TR6

TR7
TR8

TR10
TR11
TR12

TR14

TR15
TR16

BR2

BR3
BR4
BR6

BR7

BR8
BR10
BR11
BR12

BR14
BR15
BR16

BR5
BR13

Jumper jpVDD1 (see picture below) is a three pin jumper where the center pin can be shorted to either the left or right pin. Installing a short between center and left pin connects VDD1 to VBUS. Installing a short between center and right pin connects VDD1 to VSYS.

The on board isolated DC/DC converter is powered directly from the VBUS pin. The isolated 5V output can be connected two ways using Jumpers jpVDD2 and jpVDD3. The positive output terminal on the center pin of jpVDD2 can be connected to ground by shoring it to the right pin (GND) or the VDD1 trace by shorting it to the left pin. When the positive output terminal is connected to ground the output negative terminal becomes -5V with respect to ground and is connected to the center pin of jumper jpVDD3. This -5V can be connected to VEE1 by shorting the center pin to the left pin.


The board has four power distribution rails. Two on the top and two on the bottom. The lower of the two top power rails is always connected to GND. The pins of jumper jpVDD5 determine what voltage supplies the upper half of the top rail. The center pin of jpVDD5 is connected to the upper half of the top rail. Shorting the left pin to the center connects to VDD1 and shorting the right pin to the center connects to the +3.3V supplied by the Pi Pico on board LDO.

Four pin jumper jVEE1 determines the voltage supplied to the lower of the two bottom power rails. Shorting the two center pins connects it to the VEE1 (generally -5V). Three pin jumper jpVDD4 determines the voltage supplied to the upper of the two bottom power rails. Shorting the left pin to center pin connects to GND. Shorting the right pin to center pin connects to +3.3V.

jpVDD1
Right to connect to VSYS
Left to connect to VBUS

jpVDD2
Right to connect to GND

jpVDD3
Left to connect to GND

jVEE1
Short center two pins

jpVDD4
Left to connect to GND
Right to connect to +3.3V
jpVDD5
Left to connect to VDD1
Right to connect to +3.3V

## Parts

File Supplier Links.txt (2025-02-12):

From DigiKey:
Solder paste 315-NC191LT10-ND:
https://www.digikey.com/en/products/detail/chip-quik-inc./NC191LT10/11480389?utm_adgroup=&gad_source=1
CF18JT330KCT-ND RES 330K OHM 5% 1/8W AXIAL X100 $1.68
CF18JT680KCT-ND RES 680K OHM 5% 1/8W AXIAL X100 $1.68
CF18JT220RCT-ND RES 220 OHM 5% 1/8W AXIAL  X100 $1.68
CF18JT470RCT-ND RES 470 OHM 5% 1/8W AXIAL  X100 $1.68
445-180818-1-ND CAP CER 0.47UF 25V X7R RADIAL X50
CRE1S0505SC DC DC CONVERTER 5V 1W 811-3196-ND $2.37
RFM-0505S 5V isolated DC/DC converter
MCP4822 -E-P Dual Serial DAC 
MCP6004 -E-P Quad OP-AMP 
RPC8345-ND #2-56 nylon machine screws	
RPC7088-ND #2-56 nylon hex nuts

From Addicore:
10k Ohm White Knob Potentiometer
https://www.addicore.com/collections/variable-potentiometers/products/10k-ohm-white-knob-potentiometer

GS-050 50 tie point power strip
https://testequipmentusa.com/global-specialties-gs-050-bus-strip-50-tie-points-2-pack/?srsltid=AfmBOoqYwnTtbbMpz2YXtguHqOQdgc8ISB8xP6XhBymY_txFHgstTdrepoo

From Aliexpress:
RP-2040 Pi Pico boards
https://www.aliexpress.us/item/3256806917806174.html?
Color: RP2040 Type-C 4MB or Color: RP2040 Micro Type-C

1-10PCS SYB-170 Mini Solderless Prototype Breadboard
https://www.aliexpress.us/item/3256806379892335.html?

2-100Pcs CH446Q SMT LQFP-44 8x16 Matrix Analog Switch Array
https://www.aliexpress.us/item/3256806513688648.html?

5-500Pcs Pogo Pin Connector Pogopin Spring Loaded Through Hole 3mm
https://www.aliexpress.us/item/2255800849772402.html?
100Pcs Pogo Pin Connector Pogopin Spring Loaded Contact 3mm
https://www.aliexpress.us/item/3256807321702895.html?

Single row female header: 1X8
https://www.aliexpress.us/item/3256803241779203.html?
https://www.aliexpress.us/item/3256805226022984.html?

Dual row female header: 2X8
https://www.aliexpress.us/item/3256805948524386.html?
https://www.aliexpress.us/item/3256804148274564.html?

Dual row right angle female: 2X6
https://www.aliexpress.us/item/3256806810764627.html?
https://www.aliexpress.us/item/2255800144094493.html?

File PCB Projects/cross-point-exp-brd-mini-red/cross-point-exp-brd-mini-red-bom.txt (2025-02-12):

Reference Value Type
C1 0.56u Capacitor
C2 10u Capacitor
C3 0.56u Capacitor
C4 0.56u Capacitor
C5 0.56u Capacitor
C6 0.56u Capacitor
C7 10u Capacitor
C8 10u Capacitor

DC1 RFM-0505S or CRE1S0505SC 5V isolated DC/DC converter

J1, J2, J7, J8 1x8 Pin Female Connector Or single 2x8 for J7,8
J3, J4 pogo pins through hole 2x17 3mm
J5, J6 Solderless Power Rail 2 X 5x5 

JpVDD1, JpVDD2, JpVDD3, JpVDD4, JpVDD5 1x3 Pin Male Connector PinHeader
JVEE1 1x4 Pin Male Connector PinHeader
PMOD1 2x6 Right Angle Female PinHeader

R1 220 Resistor
R2 220 Resistor
R3 220 Resistor

R4 330k Resistor
R6 330k Resistor
R8 330k Resistor

R5 680k Resistor
R7 680k Resistor
R9 680k Resistor

R12 470 Resistor

RV1 10k Potentiometer

R10 DNP optional 1.2k Resistor
R11 DNP optional 4.7k Resistor

U1 CH446DS1 LQFP44
U2 CH446DS1 LQFP44
U3 CH446DS1 LQFP44
U4 CH446DS1 LQFP44
U5 CH446DS1 LQFP44
U9 Pico MCU_Raspberry Pi RP-2049
U10 MCP4822 DIP-8
U11 MCP6004 DIP-14

nylon machine screws RPC8345-ND #2-56	
nylon hex nuts RPC7088-ND #2-56

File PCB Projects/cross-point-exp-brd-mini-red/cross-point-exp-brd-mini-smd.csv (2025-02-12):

# | Reference | Qty | Value | Footprint | DNP
1 | C1, C2, C3, C4, C5, C6, C7, C8 | 8 | 0.22u | Capacitor_THT:C_Rect_L7.0mm_W2.0mm_P5.00mm
2 | CE1, GND1, TP6 | 3 | TestPoint | TestPoint:TestPoint_THTPad_D1.5mm_Drill0.7mm
3 | DC1 | 1 | CME0505S3C | Connector_PinHeader_2.54mm:PinHeader_1x04_P2.54mm_Vertical
4 | GND2, VCC1, VDD2, VEE1 | 4 | TestPoint | TestPoint:TestPoint_THTPad_D2.0mm_Drill1.0mm
5 | J1, J2, J7, J8 | 4 | Conn_01x08_Pin | Connector_PinHeader_2.54mm:PinHeader_1x08_P2.54mm_Vertical
6 | J3, J4 | 2 | Solderless_mini_2Rows-17Pins | Library:Solderless_mini_th_pogo_2x17_P2.54mm
7 | J5, J6 | 2 | Solderless_power-4Pins | Library:Solderless_power_2x4_P2.54mm
8 | JP1 | 1 | SolderJumper_3_Open | Jumper:SolderJumper-3_P1.3mm_Open_RoundedPad1.0x1.5mm_NumberLabels
9 | JP3, JP4 | 2 | SolderJumper_2_Open | Jumper:SolderJumper-2_P1.3mm_Open_RoundedPad1.0x1.5mm
10 | JpVDD1, JpVDD2, JpVDD3, JpVDD4, JpVDD5 | 5 | Conn_01x03_Pin | Connector_PinHeader_2.54mm:PinHeader_1x03_P2.54mm_Vertical
11 | JVEE1 | 1 | Conn_01x04_Pin | Connector_PinHeader_2.54mm:PinHeader_1x04_P2.54mm_Vertical
12 | PMOD1 | 1 | Conn_02x06_Top_Bottom | Library:PMOD_Header_2x06_P2.54mm
13 | R1, R2, R3 | 3 | 220 | Resistor_THT:R_Axial_DIN0204_L3.6mm_D1.6mm_P7.62mm_Horizontal
14 | R4, R6, R8 | 3 | 330k | Resistor_THT:R_Axial_DIN0204_L3.6mm_D1.6mm_P7.62mm_Horizontal
15 | R5, R7, R9 | 3 | 680k | Resistor_THT:R_Axial_DIN0204_L3.6mm_D1.6mm_P7.62mm_Horizontal
16 | R10 | 1 | 1.2k | Resistor_THT:R_Axial_DIN0204_L3.6mm_D1.6mm_P7.62mm_Horizontal
17 | R11 | 1 | 4.7k | Resistor_THT:R_Axial_DIN0204_L3.6mm_D1.6mm_P7.62mm_Horizontal
18 | R12 | 1 | 510 | Resistor_THT:R_Axial_DIN0204_L3.6mm_D1.6mm_P7.62mm_Horizontal
19 | RV1 | 1 | 10k | Potentiometer_THT:Potentiometer_Bourns_3386P_Vertical
20 | U1, U2, U3, U4, U5 | 5 | ~ | JumperlessFootprints:LQFP44_Tight
21 | U9 | 1 | Pico | MCU_RaspberryPi_and_Boards:RPi_Pico_SMD_TH
22 | U10 | 1 | MCP4822 | Package_DIP:DIP-8_W7.62mm
23 | U11 | 1 | MCP6004 | Package_DIP:DIP-14_W7.62mm

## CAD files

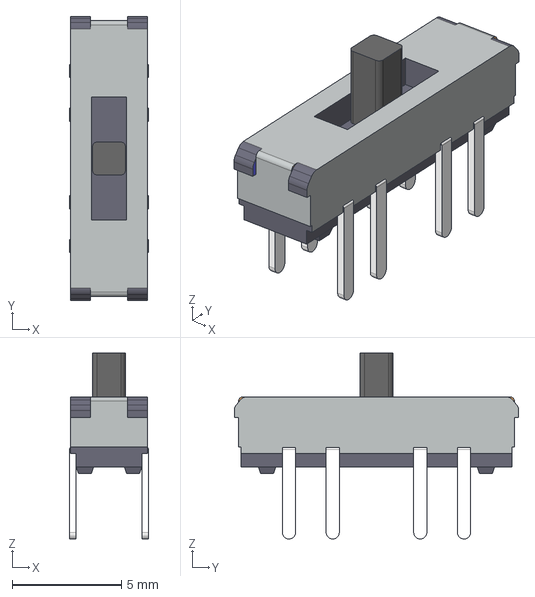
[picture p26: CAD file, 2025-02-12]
PCB Projects/cross-point-exp-brd-mini-blue/Symbols and Footprints/3dmodels/SSSS223600.step
3.60 x 13.0 x 8.50 mm

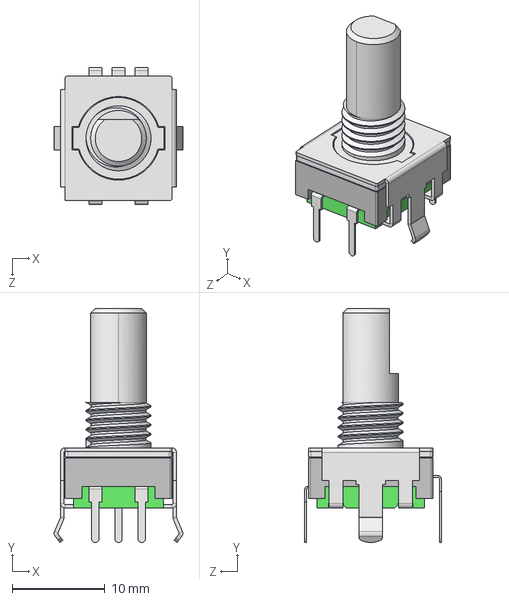
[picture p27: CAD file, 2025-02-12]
PCB Projects/cross-point-exp-brd-mini-red/Symbols and Footprints/3dmodels/PEC11R-4215F-S0024--3DModel-STEP-56544.STEP
13.9 x 25.2 x 14.7 mm

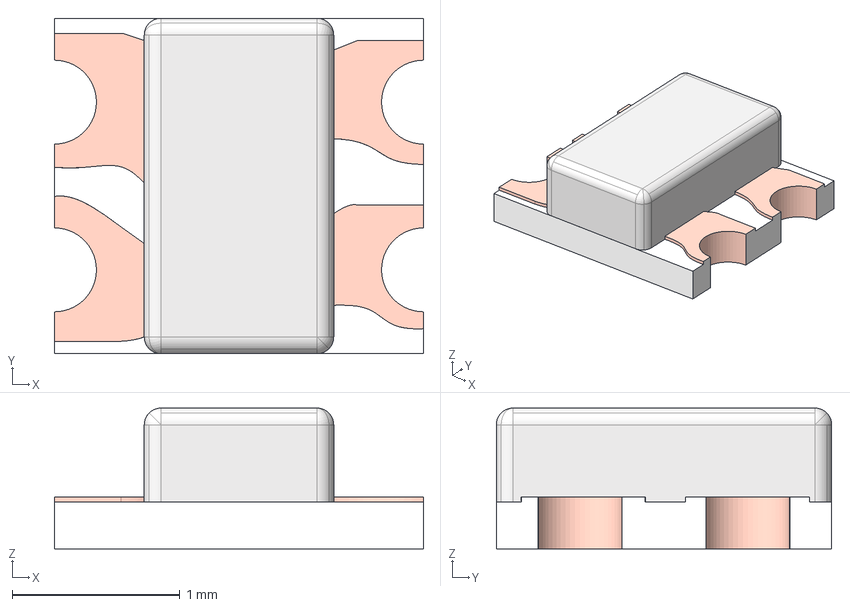
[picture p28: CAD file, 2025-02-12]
PCB Projects/cross-point-exp-brd-mini-blue/Symbols and Footprints/3dmodels/WS2812C-2020_Color.step
2.20 x 2.00 x 0.84 mm
ws2812c-2020 v2.step
ws2812c-2020 v2

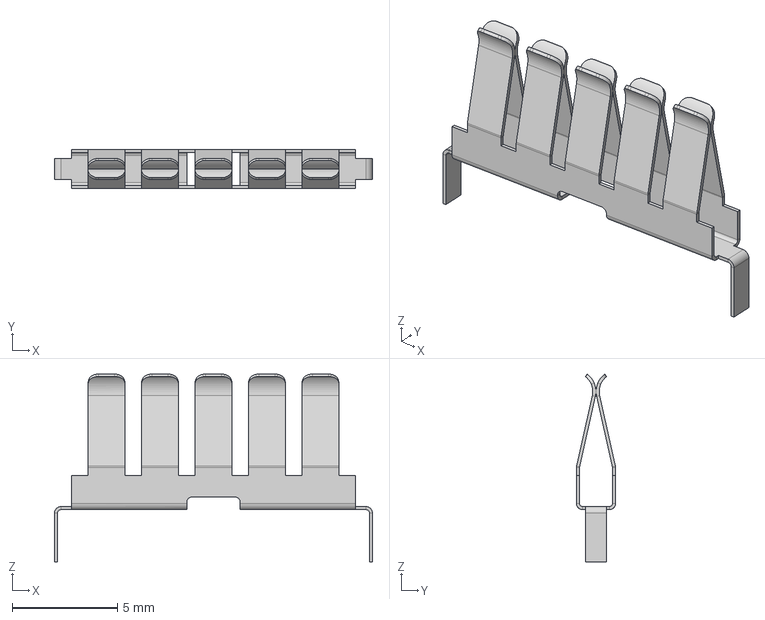
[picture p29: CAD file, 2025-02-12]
PCB Projects/cross-point-exp-brd-mini-red/Symbols and Footprints/3dmodels/bbSimple v1.step
15.1 x 1.86 x 8.92 mm

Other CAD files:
PCB Projects/cross-point-exp-brd-mini-red2/Symbols and Footprints/3dmodels/bbSimple v8.step
PCB Projects/cross-point-exp-brd-mini-red/Symbols and Footprints/3dmodels/bbSimple v8.step
PCB Projects/cross-point-exp-brd-mini-blue/Symbols and Footprints/3dmodels/bbSimple v8.step

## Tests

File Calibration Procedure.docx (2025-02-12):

How to Calibrate Software Configurable Solderless Bread boards:

These steps can also be used to calibrate any external resistor divider that might be used in conjunction with a data acquisition board that is controlled using the ALICE Universal software. It is strongly recommended that you read and understand this entire document before attempting to calibrate your target hardware.

Required Material:

1. A Digital Multimeter (hand-held DMM).

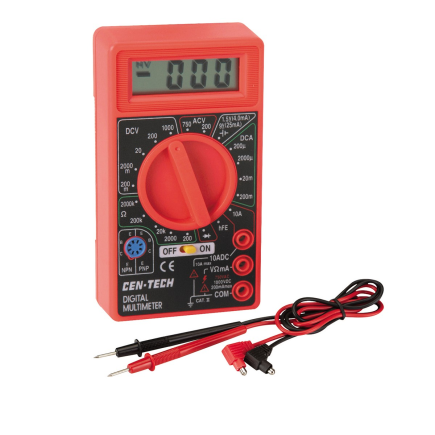
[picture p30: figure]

On Board Voltage Reference Value:

This step is generally a good idea even when not using input voltage dividers. The RP-2040 microcontroller on the board uses the 3.3V VDD LDO power supply voltage as the reference for the ADC. If the external DAC is included it has its own internal reference voltage (4.096 V). The on board 3.3 V LDO is generally accurate to +/- 20 mV. As a first check it is recommended to measure this voltage using the DMM. The 3.3V supply voltage can be measured on the right most pin of jumper jpVDD4 as shown in figure 1.

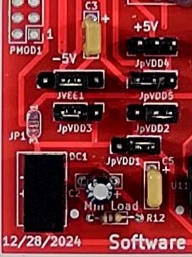
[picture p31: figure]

jpVDD4

Left most pin is GND Right most pin is +3.3V

Figure 1, Where to measure 3.3V supply voltage.

The Interface Level .py file(s) contains a variable that the ALICE software uses to “calibrate” the raw voltage measurements. You can edit this file and adjust these variables to reflect your measured results. For example, open the Pico_crosspoint-mini-red.py file in an editor and scroll down and change this line from the default value:

ADC_Cal = 3.299

The ADC_Cal variable adjusts the ADC input voltage conversion factor.

The AWGPeakToPeak variable adjusts the DAC output voltage conversion factor and can generally be left set to the default value of 4.095.

The next step is to adjust the Scope input resistor divider Offset voltage using RV1 as shown on the left side of figure 2. The Scope Input and AWG Output 2X8 pin female header is shown on the right side along with the six voltage divider resistors. Generally the Low sides of the resistor dividers are shorted to the offset voltage as shown using jumpers.

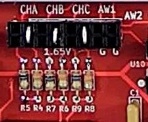
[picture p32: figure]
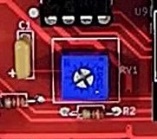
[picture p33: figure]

Offset Voltage Adjust Pot

Offset Voltage on left 6 pins of bottom row

Ground is on the right 2 pins of bottom row

AWG 1 Output Voltage

Figure 2, Adjusting the Offset Voltage.

Conned the DMM across any one of the two Ground pins and any one the 6 Offset voltage pins. The 680kΩ / 330kΩ resistor divider ratio is 1010/330 or 3.06. Multiplied by the 0 to 3.3 V ADC input range gives a P-P range of 10.1 V total. By adjusting the Offset voltage to 2.5 V we can center this range on 0V for a measurement range of approximately -5 V to +5 V which is perfect for the +/- 5V power supply of the Matrix analog switches. Adjust RV1 for a reading of 2.500 V on the DMM.

Using the ALICE software Gain and Offset adjustment settings:

The first step is to open the Input divider calculator by clicking on the Adjust Gain / Offset button. The Divider calculator tool screen will open as shown in figure 3.

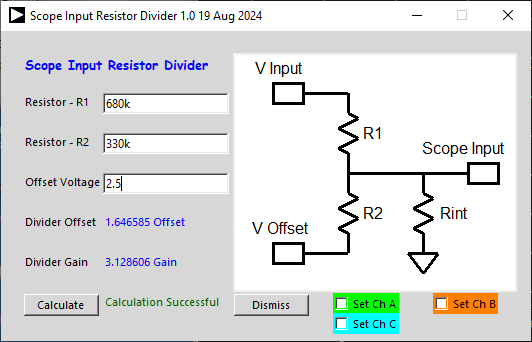
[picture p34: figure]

Figure 3, Input divider calculator.

Enter values for R1, 680k and R2, 330k and the offset voltage, 2.5. Click the Calculate button. The offset and gain values will now be filled in. To transfer these values to the Ch A, Ch B and Ch C entries click on the three Set check boxes. These approximate values should now be populated as shown.

These values are of course only approximately correct for your specific board given the tolerance in the actual resistor values used on your board. The next step is to calibrate (adjust) the actual Gain and Offset values.

We will be using the AWG1 signal generator output as our calibration standard. We can use the Cross Point switches to connect the Scope inputs to the AWG1 output using the Cross Point Interface Screen. We can connect the three Scope inputs (AINH, BINH and CINH) and the AWG output (AWG1) together using Jumper JP1. Enter JP1 in Jumper, and 1 in On/Off. To connect the AWG1 output to jumper JP1 enter AWG1 in Comp Pin. Click the Set button. Repeat for the three Scope inputs by entering AINH, BINH and CINH for Comp Pin one at a time and click the Set button.

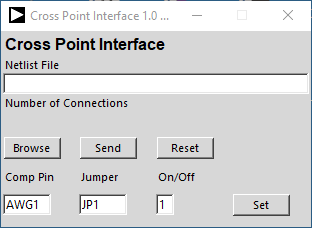
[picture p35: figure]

Enter Name of Component Pin Here

Enter Name of Jumper Here

Enter

1 to close switch connection

0 to open switch connection

Click Set to make / break connection

Reset opens all switches

The three Scope input channels should now be connected to the AWG1 signal generator output.

Now we need to configure the AWG CH A settings as per the figure below. Set the waveform shape to Sine. Set the Low V value to 0.0 (the DAC minimum output voltage). Set the High V value to 4.0 (a close to full scale round number for the DAC). The Freq can be set to just about any value but 300 Hz is a good number. Click the AWG A Output OFF button to ON to start generating the waveform.

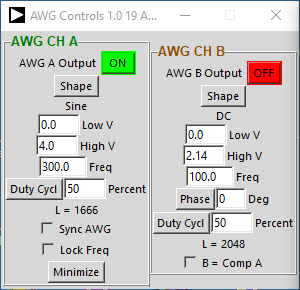
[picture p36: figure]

Set Shape to Sine

Set Low V to 0.0

Set High V to 4.0

Set Freq to 300

With just the CH A, CH B and CH C traces selected, Click Run. Use CH A as the trigger source and center the trigger level on the waveform. Adjust the channel range and position settings to center the waveforms on the screen. 500mV/div and 2.5 for the Pos are good options. A time scale of 1mS / Div is also a good setting. Turn on trace averaging using the ‘a’ key on the key board.

We first want to adjust the Gain for each channel such that the peak to peak value matches the 4 Vp-p from the AWG generator. From the Meas drop down menus select p-p for all three channels. Tweak the values in the Gain entries for each channel until you measure as close to 4.00 V p-p as possible.

Tweaked Values

To adjust the offset we need to set the AWG output to 0V DC. Change the waveform shape to DC and the High V value to 0.0. From the Meas drop down menus select Avg for all three channels. Tweak the values in the Offset entries for each channel until you measure as close to 0.00 V avg as possible.

Your Scope input channels should now be calibrated to match the accuracy of the DAC.

These adjustment settings are automatically saved in the alice-last-config.cfg file along with all the other configuration settings each time you exit ALICE. You can also save just the input gain and offset adjustment values in a separate file by clicking on the Save Adj button in the File Drop down menu. Clicking on the Load Adj button will load the saved values from the file.

Appendix:

For additional accuracy the DAC Full Scale voltage can be checked with the DMM. Set the AWG A High V to 4.00 and the Shape to DC. The DAC output can be accessed on the upper row second from the right pin as in figure 2. When calibrating the Input channel gain we assumed that the DAC output was exactly 4.00 V p-p. Using this actual measured peak voltage for the DAC output will provide a more accurate calibration.

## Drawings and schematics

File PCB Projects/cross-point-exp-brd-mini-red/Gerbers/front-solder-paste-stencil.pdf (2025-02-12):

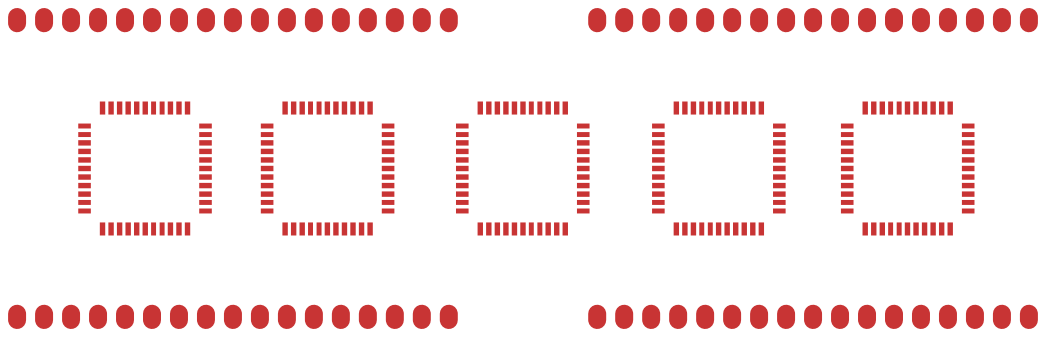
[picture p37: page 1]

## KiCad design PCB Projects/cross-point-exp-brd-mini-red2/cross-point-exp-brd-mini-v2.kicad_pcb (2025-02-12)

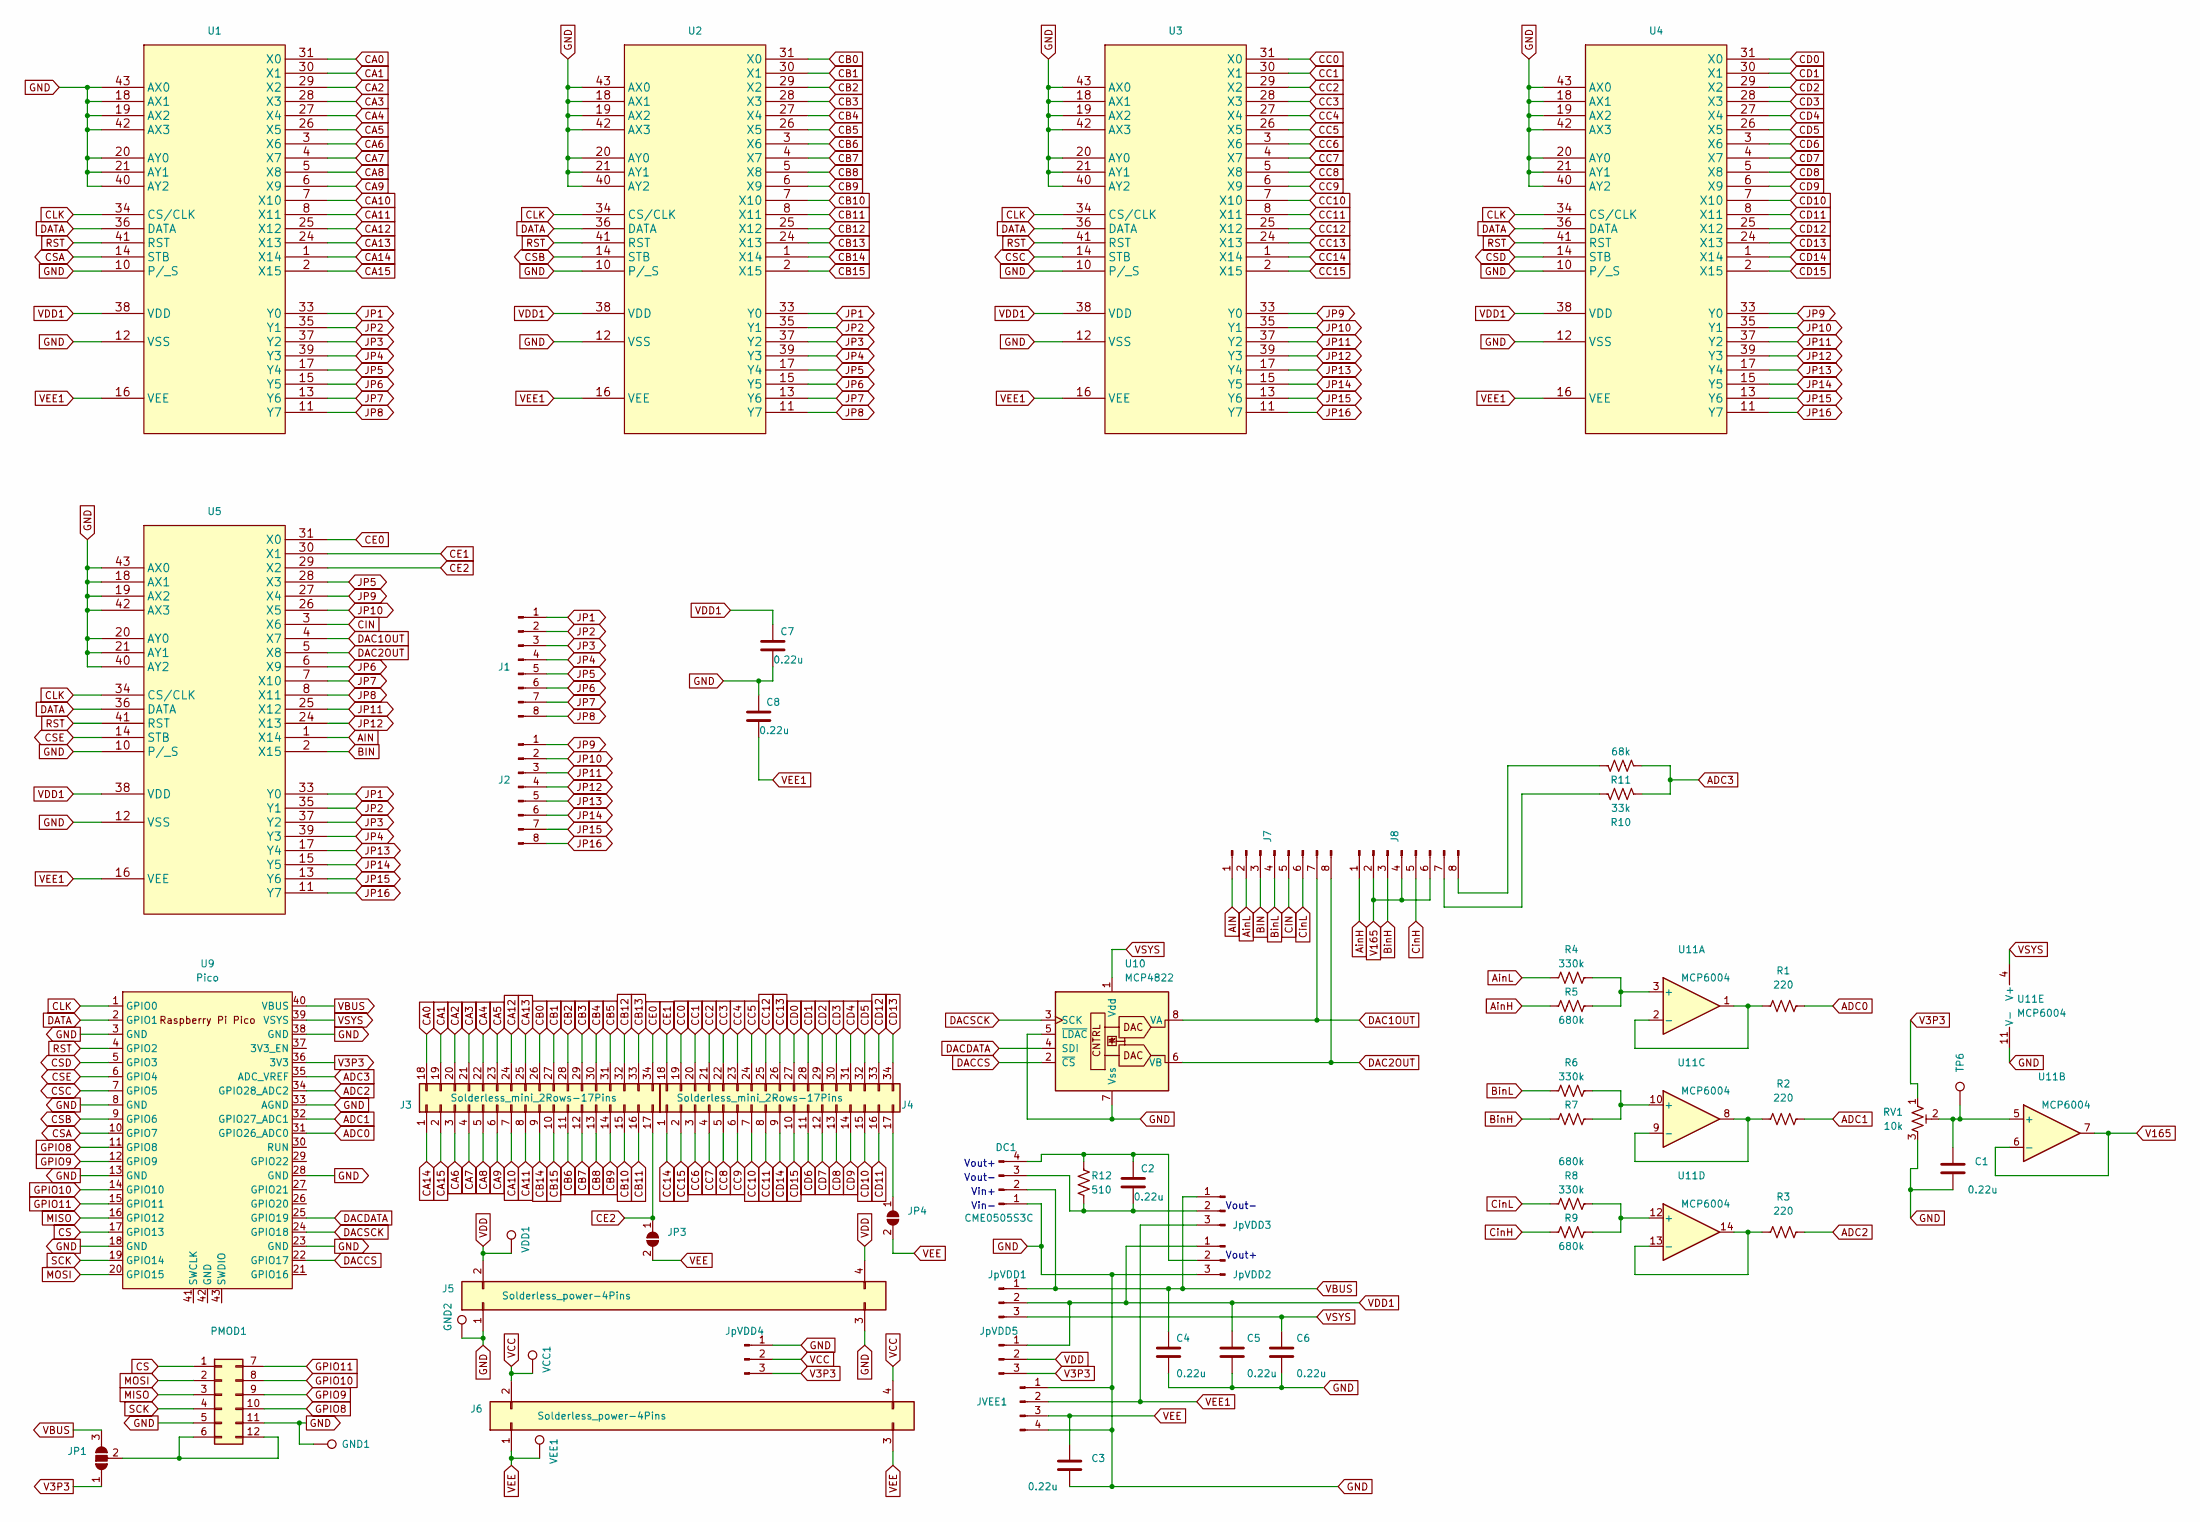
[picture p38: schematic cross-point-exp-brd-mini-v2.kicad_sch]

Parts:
C1, C2, C3, C4, C5, C6, C7, C8: 0.22u; C_Rect_L7.0mm_W2.0mm_P5.00mm
DC1: CME0505S3C; PinHeader_1x04_P2.54mm_Vertical
GND1: TestPoint; TestPoint_THTPad_D1.5mm_Drill0.7mm
GND2: TestPoint; TestPoint_THTPad_D2.0mm_Drill1.0mm
J1, J2, J7, J8: Conn_01x08_Pin; PinHeader_1x08_P2.54mm_Vertical
J3, J4: Solderless_mini_2Rows-17Pins; Solderless_mini_th_pogo_2x17_P2.54mm
J5, J6: Solderless_power-4Pins; Solderless_power_2x4_P2.54mm
JP1: SolderJumper_3_Open; SolderJumper-3_P1.3mm_Open_RoundedPad1.0x1.5mm_NumberLabels
JP3, JP4: SolderJumper_2_Open; SolderJumper-2_P1.3mm_Open_RoundedPad1.0x1.5mm
JVEE1: Conn_01x04_Pin; PinHeader_1x04_P2.54mm_Vertical
JpVDD1, JpVDD2, JpVDD3, JpVDD4, JpVDD5: Conn_01x03_Pin; PinHeader_1x03_P2.54mm_Vertical
PMOD1: Conn_02x06_Top_Bottom; PMOD_Header_2x06_P2.54mm
R1, R2, R3: 220; R_Axial_DIN0204_L3.6mm_D1.6mm_P7.62mm_Horizontal
R4, R6, R8: 330k; R_Axial_DIN0204_L3.6mm_D1.6mm_P7.62mm_Horizontal
R5, R7, R9: 680k; R_Axial_DIN0204_L3.6mm_D1.6mm_P7.62mm_Horizontal
R10: 33k; R_Axial_DIN0204_L3.6mm_D1.6mm_P7.62mm_Horizontal
R11: 68k; R_Axial_DIN0204_L3.6mm_D1.6mm_P7.62mm_Horizontal
R12: 510; R_Axial_DIN0204_L3.6mm_D1.6mm_P7.62mm_Horizontal
RV1: 10k; Potentiometer_Bourns_3386P_Vertical
TP6: TestPoint; TestPoint_THTPad_D1.5mm_Drill0.7mm
U1, U2, U3, U4, U5: LQFP44_Tight
U9: Pico; RPi_Pico_SMD_TH
U10: MCP4822; DIP-8_W7.62mm
U11: MCP6004; DIP-14_W7.62mm
VCC1: TestPoint; TestPoint_THTPad_D2.0mm_Drill1.0mm
VDD1: TestPoint; TestPoint_THTPad_D2.0mm_Drill1.0mm
VEE1: TestPoint; TestPoint_THTPad_D2.0mm_Drill1.0mm

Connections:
ADC0: R1.1, U9.31 (GPIO26_ADC0)
ADC1: R2.1, U9.32 (GPIO27_ADC1)
ADC2: R3.1, U9.34 (GPIO28_ADC2)
ADC3: R10.1, R11.1, U9.35 (ADC_VREF)
AIN: J7.1, U5.1 (X14)
AinH: J8.1, R5.2
AinL: J7.2, R4.2
BIN: J7.3, U5.2 (X15)
BinH: J8.3, R7.2
BinL: J7.4, R6.2
CA0: J3.18, U1.31 (X0)
CA1: J3.19, U1.30 (X1)
CA2: J3.20, U1.29 (X2)
CA3: J3.21, U1.28 (X3)
CA4: J3.22, U1.27 (X4)
CA5: J3.23, U1.26 (X5)
CA6: J3.3, U1.3 (X6)
CA7: J3.4, U1.4 (X7)
CA8: J3.5, U1.5 (X8)
CA9: J3.6, U1.6 (X9)
CA10: J3.7, U1.7 (X10)
CA11: J3.8, U1.8 (X11)
CA12: J3.24, U1.25 (X12)
CA13: J3.25, U1.24 (X13)
CA14: J3.1, U1.1 (X14)
CA15: J3.2, U1.2 (X15)
CB0: J3.26, U2.31 (X0)
CB1: J3.27, U2.30 (X1)
CB2: J3.28, U2.29 (X2)
CB3: J3.29, U2.28 (X3)
CB4: J3.30, U2.27 (X4)
CB5: J3.31, U2.26 (X5)
CB6: J3.11, U2.3 (X6)
CB7: J3.12, U2.4 (X7)
CB8: J3.13, U2.5 (X8)
CB9: J3.14, U2.6 (X9)
CB10: J3.15, U2.7 (X10)
CB11: J3.16, U2.8 (X11)
CB12: J3.32, U2.25 (X12)
CB13: J3.33, U2.24 (X13)
CB14: J3.9, U2.1 (X14)
CB15: J3.10, U2.2 (X15)
CC0: J4.19, U3.31 (X0)
CC1: J4.20, U3.30 (X1)
CC2: J4.21, U3.29 (X2)
CC3: J4.22, U3.28 (X3)
CC4: J4.23, U3.27 (X4)
CC5: J4.24, U3.26 (X5)
CC6: J4.3, U3.3 (X6)
CC7: J4.4, U3.4 (X7)
CC8: J4.5, U3.5 (X8)
CC9: J4.6, U3.6 (X9)
CC10: J4.7, U3.7 (X10)
CC11: J4.8, U3.8 (X11)
CC12: J4.25, U3.25 (X12)
CC13: J4.26, U3.24 (X13)
CC14: J4.1, U3.1 (X14)
CC15: J4.2, U3.2 (X15)
CD0: J4.27, U4.31 (X0)
CD1: J4.28, U4.30 (X1)
CD2: J4.29, U4.29 (X2)
CD3: J4.30, U4.28 (X3)
CD4: J4.31, U4.27 (X4)
CD5: J4.32, U4.26 (X5)
CD6: J4.11, U4.3 (X6)
CD7: J4.12, U4.4 (X7)
CD8: J4.13, U4.5 (X8)
CD9: J4.14, U4.6 (X9)
CD10: J4.15, U4.7 (X10)
CD11: J4.16, U4.8 (X11)
CD12: J4.33, U4.25 (X12)
CD13: J4.34, U4.24 (X13)
CD14: J4.9, U4.1 (X14)
CD15: J4.10, U4.2 (X15)
CE0: J3.34, U5.31 (X0)
CE1: J4.18, U5.30 (X1)
CE2: J3.17, JP3.1 (A), U5.29 (X2)
CIN: J7.5, U5.3 (X6)
CLK: U1.34 (CS/CLK), U2.34 (CS/CLK), U3.34 (CS/CLK), U4.34 (CS/CLK), U5.34 (CS/CLK), U9.1 (GPIO0)
CS: PMOD1.1, U9.17 (GPIO13)
CSA: U1.14 (STB), U9.10 (GPIO7)
CSB: U2.14 (STB), U9.9 (GPIO6)
CSC: U3.14 (STB), U9.7 (GPIO5)
CSD: U4.14 (STB), U9.5 (GPIO3)
CSE: U5.14 (STB), U9.6 (GPIO4)
CinH: J8.5, R9.2
CinL: J7.6, R8.2
DAC1OUT: J7.7, U5.4 (X7), U10.8 (VA)
DAC2OUT: J7.8, U5.5 (X8), U10.6 (VB)
DACCS: U9.22 (GPIO17), U10.2 (~CS)
DACDATA: U9.25 (GPIO19), U10.4 (SDI)
DACSCK: U9.24 (GPIO18), U10.3 (SCK)
DATA: U1.36 (DATA), U2.36 (DATA), U3.36 (DATA), U4.36 (DATA), U5.36 (DATA), U9.2 (GPIO1)
GND: C1.2, C3.2, C4.2, C5.2, C6.2, C7.2, C8.1, DC1.1, GND1.1, GND2.1, J5.1, J5.3, JVEE1.1, JVEE1.4, JpVDD2.3, JpVDD4.1, PMOD1.5, PMOD1.11, RV1.3, U1.10 (P/_S), U1.12 (VSS), U1.18 (AX1), U1.19 (AX2), U1.20 (AY0), U1.21 (AY1), U1.40 (AY2), U1.42 (AX3), U1.43 (AX0), U2.10 (P/_S), U2.12 (VSS), U2.18 (AX1), U2.19 (AX2), U2.20 (AY0), U2.21 (AY1), U2.40 (AY2), U2.42 (AX3), U2.43 (AX0), U3.10 (P/_S), U3.12 (VSS), U3.18 (AX1), U3.19 (AX2), U3.20 (AY0), U3.21 (AY1), U3.40 (AY2), U3.42 (AX3), U3.43 (AX0), U4.10 (P/_S), U4.12 (VSS), U4.18 (AX1), U4.19 (AX2), U4.20 (AY0), U4.21 (AY1), U4.40 (AY2), U4.42 (AX3), U4.43 (AX0), U5.10 (P/_S), U5.12 (VSS), U5.18 (AX1), U5.19 (AX2), U5.20 (AY0), U5.21 (AY1), U5.40 (AY2), U5.42 (AX3), U5.43 (AX0), U9.3 (GND), U9.8 (GND), U9.13 (GND), U9.18 (GND), U9.23 (GND), U9.28 (GND), U9.33 (AGND), U9.38 (GND), U10.5 (~LDAC), U10.7 (Vss), U11.11 (V-)
GPIO8: PMOD1.10, U9.11 (GPIO8)
GPIO9: PMOD1.9, U9.12 (GPIO9)
GPIO10: PMOD1.8, U9.14 (GPIO10)
GPIO11: PMOD1.7, U9.15 (GPIO11)
JP1: J1.1, U1.33 (Y0), U2.33 (Y0), U5.33 (Y0)
JP2: J1.2, U1.35 (Y1), U2.35 (Y1), U5.35 (Y1)
JP3: J1.3, U1.37 (Y2), U2.37 (Y2), U5.37 (Y2)
JP4: J1.4, U1.39 (Y3), U2.39 (Y3), U5.39 (Y3)
JP5: J1.5, U1.17 (Y4), U2.17 (Y4), U5.28 (X3)
JP6: J1.6, U1.15 (Y5), U2.15 (Y5), U5.6 (X9)
JP7: J1.7, U1.13 (Y6), U2.13 (Y6), U5.7 (X10)
JP8: J1.8, U1.11 (Y7), U2.11 (Y7), U5.8 (X11)
JP9: J2.1, U3.33 (Y0), U4.33 (Y0), U5.27 (X4)
JP10: J2.2, U3.35 (Y1), U4.35 (Y1), U5.26 (X5)
JP11: J2.3, U3.37 (Y2), U4.37 (Y2), U5.25 (X12)
JP12: J2.4, U3.39 (Y3), U4.39 (Y3), U5.24 (X13)
JP13: J2.5, U3.17 (Y4), U4.17 (Y4), U5.17 (Y4)
JP14: J2.6, U3.15 (Y5), U4.15 (Y5), U5.15 (Y5)
JP15: J2.7, U3.13 (Y6), U4.13 (Y6), U5.13 (Y6)
JP16: J2.8, U3.11 (Y7), U4.11 (Y7), U5.11 (Y7)
MISO: PMOD1.3, U9.16 (GPIO12)
MOSI: PMOD1.2, U9.20 (GPIO15)
unnamed: C2.2, DC1.3, JpVDD3.2, R12.1
unnamed: C2.1, DC1.4, JpVDD2.2, R12.2
unnamed: J4.17, JP4.1 (A)
unnamed: J8.7, R10.2
unnamed: J8.8, R11.2
unnamed: JP1.2 (C), PMOD1.6, PMOD1.12
unnamed: R4.1, R5.1, U11.3 (+)
unnamed: R1.2, U11.1, U11.2 (-)
unnamed: C1.1, RV1.2, TP6.1, U11.5 (+)
unnamed: R6.1, R7.1, U11.10 (+)
unnamed: R2.2, U11.8, U11.9 (-)
unnamed: R8.1, R9.1, U11.12 (+)
unnamed: R3.2, U11.13 (-), U11.14
RST: U1.41 (RST), U2.41 (RST), U3.41 (RST), U4.41 (RST), U5.41 (RST), U9.4 (GPIO2)
SCK: PMOD1.4, U9.19 (GPIO14)
V3P3: JP1.1 (A), JpVDD4.3, JpVDD5.3, RV1.1, U9.36 (3V3)
V165: J8.2, J8.4, J8.6, U11.6 (-), U11.7
VBUS: C4.1, DC1.2, JP1.3 (B), JpVDD1.1, JpVDD3.1, U9.40 (VBUS)
VCC: J6.2, J6.4, JpVDD4.2, VCC1.1
VDD: J5.2, J5.4, JpVDD5.2, VDD1.1
VDD1: C5.1, C7.1, JpVDD1.2, JpVDD2.1, JpVDD5.1, U1.38 (VDD), U2.38 (VDD), U3.38 (VDD), U4.38 (VDD), U5.38 (VDD)
VEE: C3.1, J6.1, J6.3, JP3.2 (B), JP4.2 (B), JVEE1.3, VEE1.1
VEE1: C8.2, JVEE1.2, JpVDD3.3, U1.16 (VEE), U2.16 (VEE), U3.16 (VEE), U4.16 (VEE), U5.16 (VEE)
VSYS: C6.1, JpVDD1.3, U9.39 (VSYS), U10.1 (Vdd), U11.4 (V+)

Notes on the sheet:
Vin+
Vout+
Vout-
Vin-

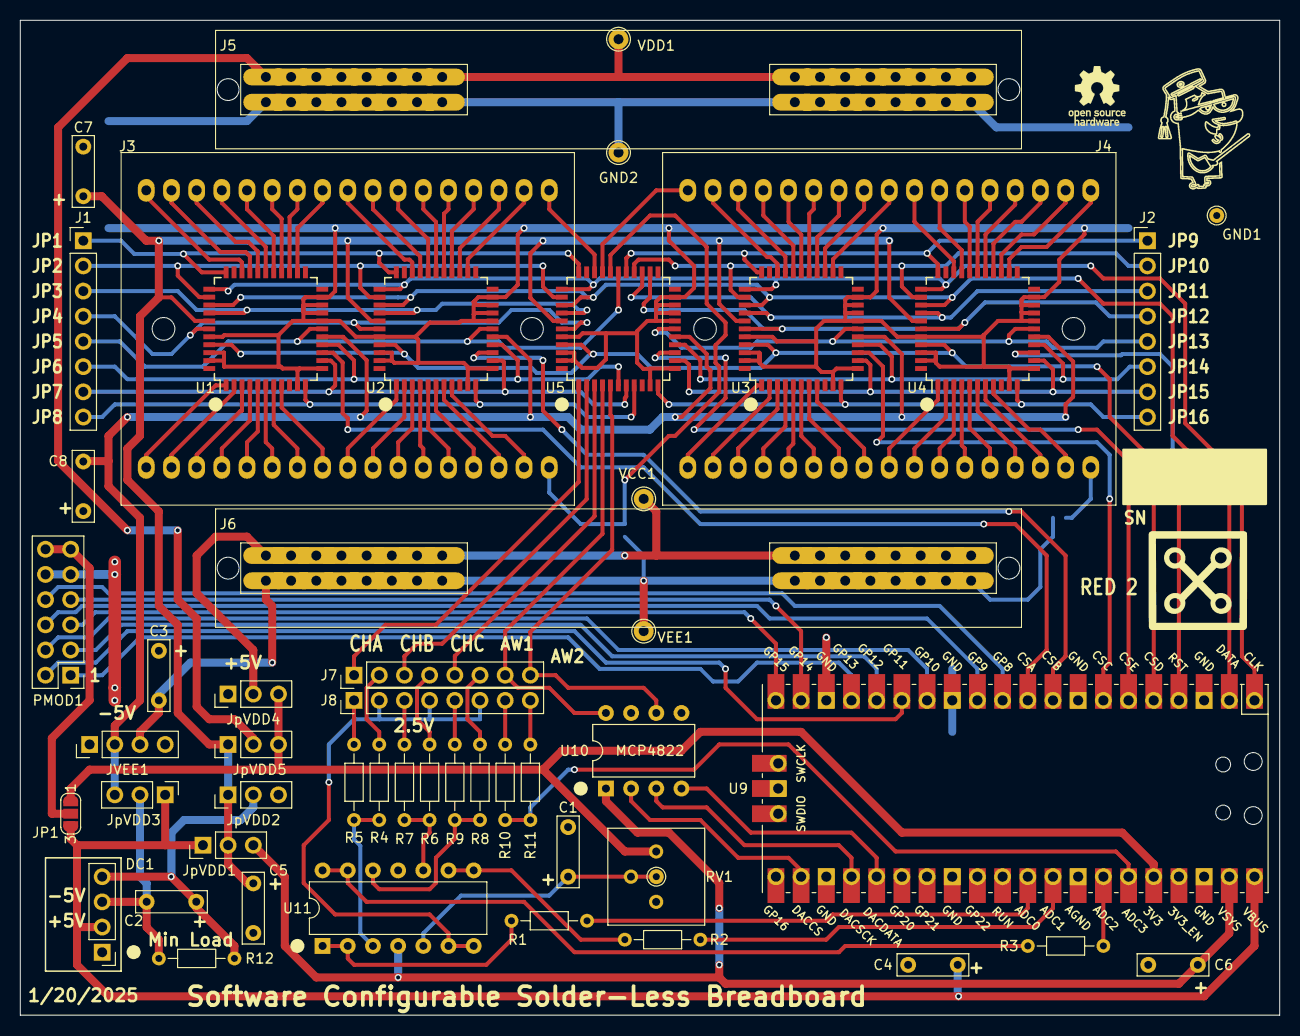
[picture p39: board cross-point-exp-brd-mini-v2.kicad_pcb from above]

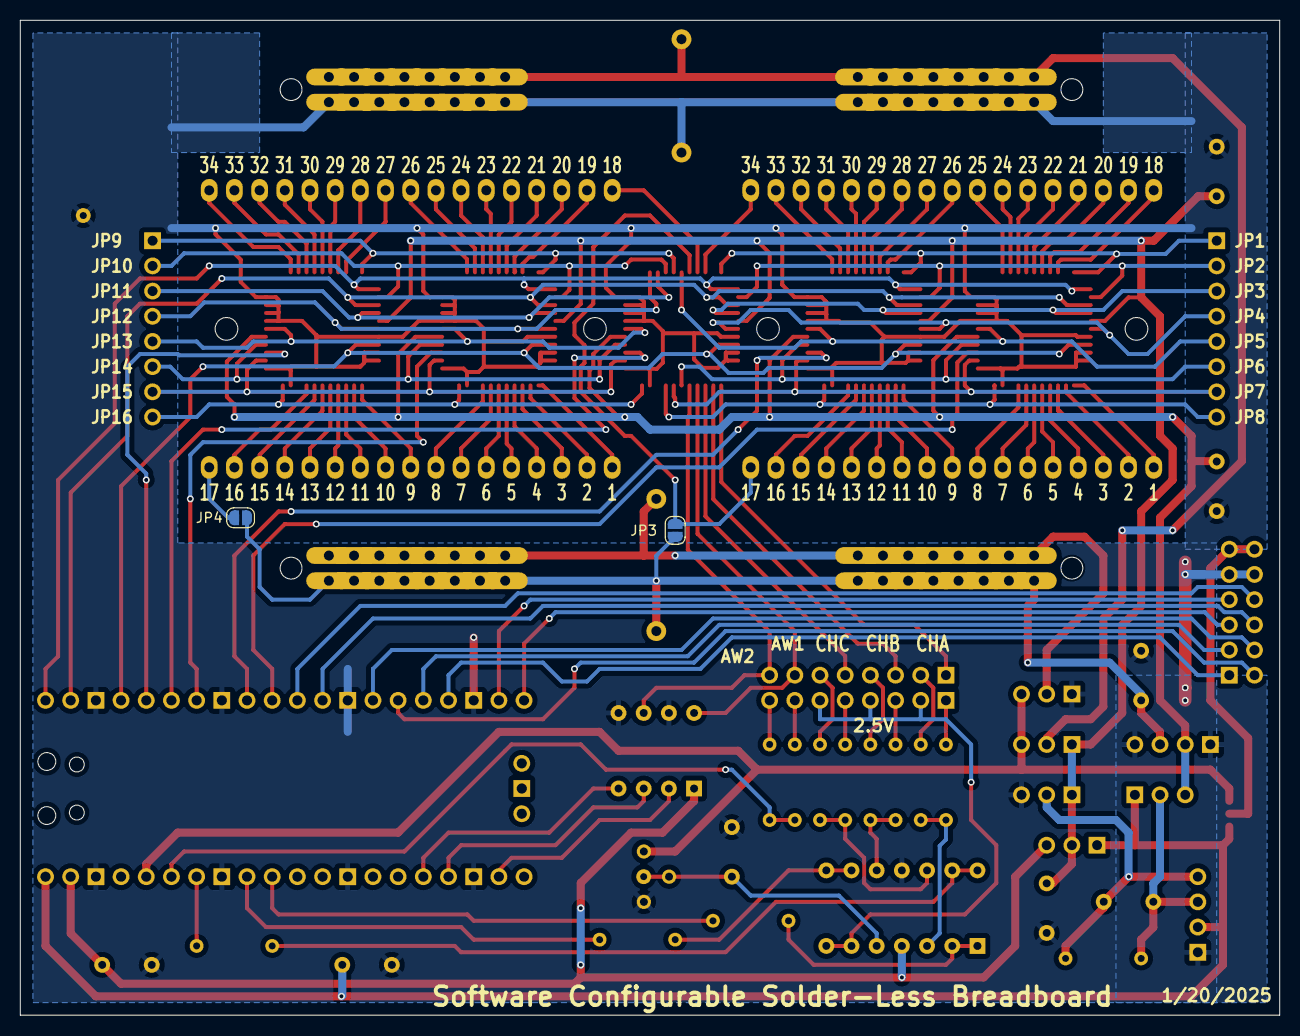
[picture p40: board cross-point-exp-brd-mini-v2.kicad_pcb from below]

Board: 2 copper layers, 127.0 x 100.3 mm, 54 parts (2 on the bottom side), 140 nets.

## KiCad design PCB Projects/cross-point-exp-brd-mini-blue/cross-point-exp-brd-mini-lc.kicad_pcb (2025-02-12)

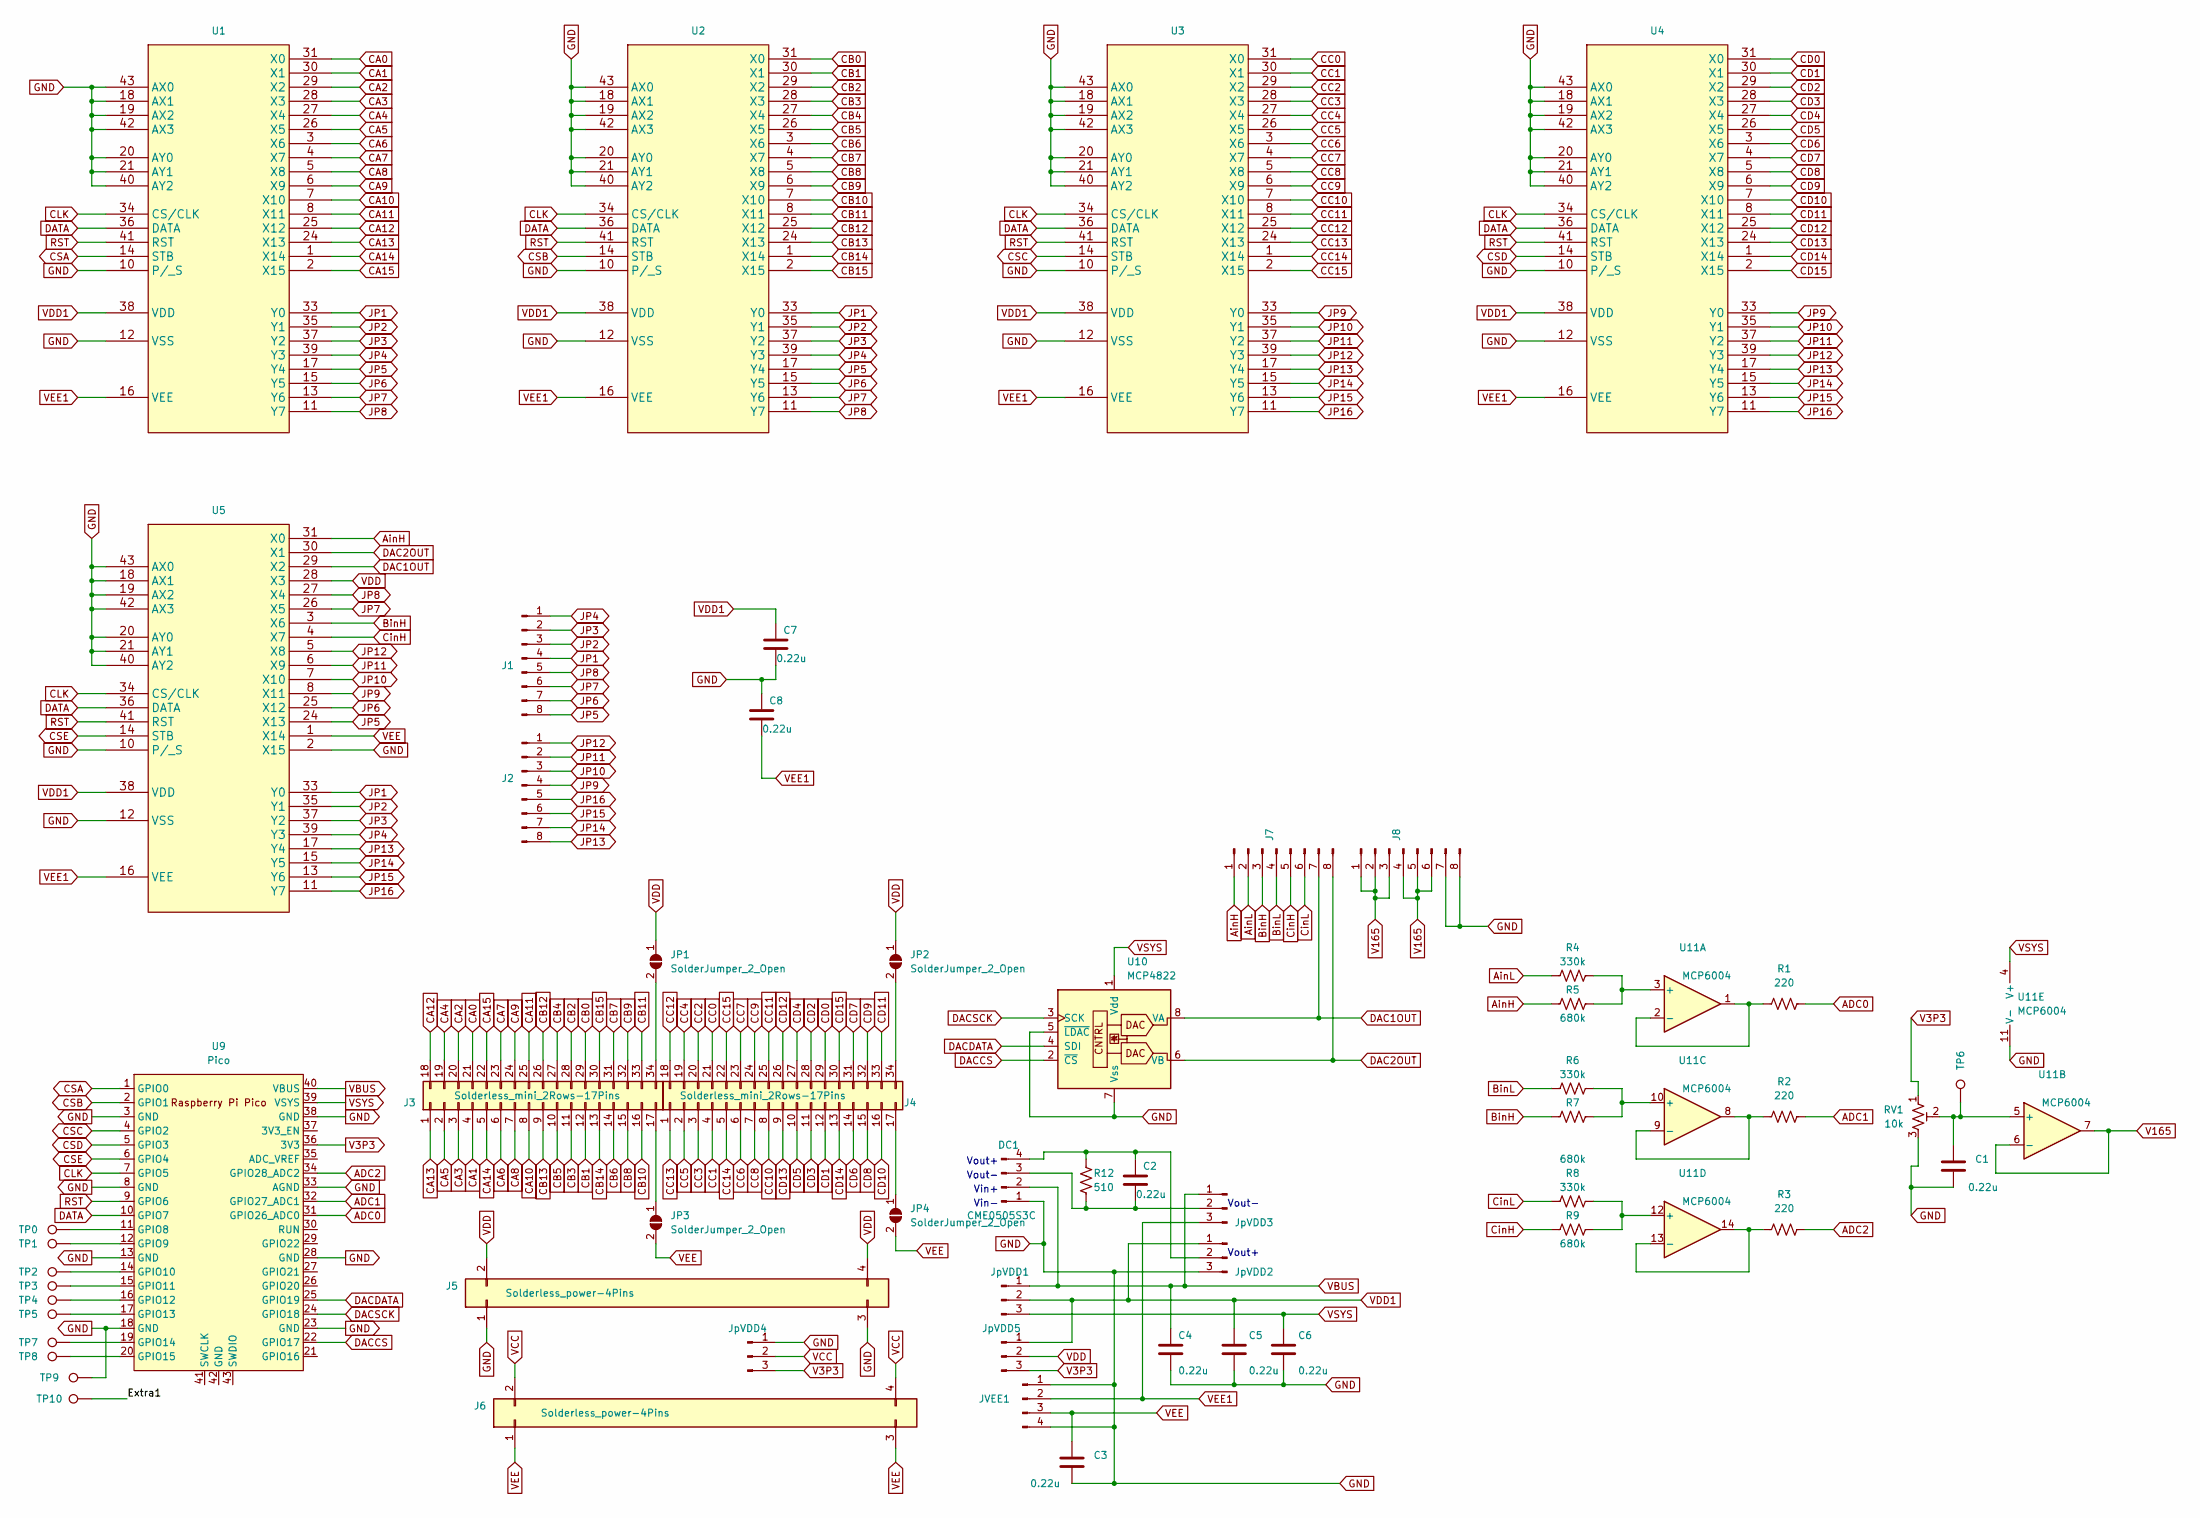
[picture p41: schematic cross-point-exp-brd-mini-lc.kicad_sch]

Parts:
C1, C2, C3, C4, C5, C6, C7, C8: 0.22u; C_Rect_L7.0mm_W2.0mm_P5.00mm
DC1: CME0505S3C; PinHeader_1x04_P2.54mm_Vertical
J1, J2, J7, J8: Conn_01x08_Pin; PinHeader_1x08_P2.54mm_Vertical
J3, J4: Solderless_mini_2Rows-17Pins; Solderless_mini_wmh_2x17_P2.54mm
J5, J6: Solderless_power-4Pins; Solderless_power_P2.54mm
JP1, JP2, JP3, JP4: SolderJumper_2_Open; SolderJumper-2_P1.3mm_Open_RoundedPad1.0x1.5mm
JVEE1: Conn_01x04_Pin; PinHeader_1x04_P2.54mm_Vertical
JpVDD1, JpVDD2, JpVDD3, JpVDD4, JpVDD5: Conn_01x03_Pin; PinHeader_1x03_P2.54mm_Vertical
R1, R2, R3: 220; R_Axial_DIN0204_L3.6mm_D1.6mm_P7.62mm_Horizontal
R4, R6, R8: 330k; R_Axial_DIN0204_L3.6mm_D1.6mm_P7.62mm_Horizontal
R5, R7, R9: 680k; R_Axial_DIN0204_L3.6mm_D1.6mm_P7.62mm_Horizontal
R12: 510; R_Axial_DIN0204_L3.6mm_D1.6mm_P7.62mm_Horizontal
RV1: 10k; Potentiometer_Bourns_3386P_Vertical
TP0, TP1, TP2, TP3, TP4, TP5, TP6, TP7, TP8, TP9, TP10: TestPoint; TestPoint_THTPad_D1.5mm_Drill0.7mm
U1, U2, U3, U4, U5: LQFP44_Tight
U9: Pico; RPi_Pico_SMD_TH
U10: MCP4822; DIP-8_W7.62mm
U11: MCP6004; DIP-14_W7.62mm

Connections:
/Extra1: TP10.1
ADC0: R1.1, U9.31 (GPIO26_ADC0)
ADC1: R2.1, U9.32 (GPIO27_ADC1)
ADC2: R3.1, U9.34 (GPIO28_ADC2)
AinH: J7.1, R5.2, U5.31 (X0)
AinL: J7.2, R4.2
BinH: J7.3, R7.2, U5.3 (X6)
BinL: J7.4, R6.2
CA0: J3.21, U1.31 (X0)
CA1: J3.4, U1.30 (X1)
CA2: J3.20, U1.29 (X2)
CA3: J3.3, U1.28 (X3)
CA4: J3.19, U1.27 (X4)
CA5: J3.2, U1.26 (X5)
CA6: J3.6, U1.3 (X6)
CA7: J3.23, U1.4 (X7)
CA8: J3.7, U1.5 (X8)
CA9: J3.24, U1.6 (X9)
CA10: J3.8, U1.7 (X10)
CA11: J3.25, U1.8 (X11)
CA12: J3.18, U1.25 (X12)
CA13: J3.1, U1.24 (X13)
CA14: J3.5, U1.1 (X14)
CA15: J3.22, U1.2 (X15)
CB0: J3.29, U2.31 (X0)
CB1: J3.12, U2.30 (X1)
CB2: J3.28, U2.29 (X2)
CB3: J3.11, U2.28 (X3)
CB4: J3.27, U2.27 (X4)
CB5: J3.10, U2.26 (X5)
CB6: J3.14, U2.3 (X6)
CB7: J3.31, U2.4 (X7)
CB8: J3.15, U2.5 (X8)
CB9: J3.32, U2.6 (X9)
CB10: J3.16, U2.7 (X10)
CB11: J3.33, U2.8 (X11)
CB12: J3.26, U2.25 (X12)
CB13: J3.9, U2.24 (X13)
CB14: J3.13, U2.1 (X14)
CB15: J3.30, U2.2 (X15)
CC0: J4.21, U3.31 (X0)
CC1: J4.4, U3.30 (X1)
CC2: J4.20, U3.29 (X2)
CC3: J4.3, U3.28 (X3)
CC4: J4.19, U3.27 (X4)
CC5: J4.2, U3.26 (X5)
CC6: J4.6, U3.3 (X6)
CC7: J4.23, U3.4 (X7)
CC8: J4.7, U3.5 (X8)
CC9: J4.24, U3.6 (X9)
CC10: J4.8, U3.7 (X10)
CC11: J4.25, U3.8 (X11)
CC12: J4.18, U3.25 (X12)
CC13: J4.1, U3.24 (X13)
CC14: J4.5, U3.1 (X14)
CC15: J4.22, U3.2 (X15)
CD0: J4.29, U4.31 (X0)
CD1: J4.12, U4.30 (X1)
CD2: J4.28, U4.29 (X2)
CD3: J4.11, U4.28 (X3)
CD4: J4.27, U4.27 (X4)
CD5: J4.10, U4.26 (X5)
CD6: J4.14, U4.3 (X6)
CD7: J4.31, U4.4 (X7)
CD8: J4.15, U4.5 (X8)
CD9: J4.32, U4.6 (X9)
CD10: J4.16, U4.7 (X10)
CD11: J4.33, U4.8 (X11)
CD12: J4.26, U4.25 (X12)
CD13: J4.9, U4.24 (X13)
CD14: J4.13, U4.1 (X14)
CD15: J4.30, U4.2 (X15)
CLK: U1.34 (CS/CLK), U2.34 (CS/CLK), U3.34 (CS/CLK), U4.34 (CS/CLK), U5.34 (CS/CLK), U9.7 (GPIO5)
CSA: U1.14 (STB), U9.1 (GPIO0)
CSB: U2.14 (STB), U9.2 (GPIO1)
CSC: U3.14 (STB), U9.4 (GPIO2)
CSD: U4.14 (STB), U9.5 (GPIO3)
CSE: U5.14 (STB), U9.6 (GPIO4)
CinH: J7.5, R9.2, U5.4 (X7)
CinL: J7.6, R8.2
DAC1OUT: J7.7, U5.29 (X2), U10.8 (VA)
DAC2OUT: J7.8, U5.30 (X1), U10.6 (VB)
DACCS: U9.22 (GPIO17), U10.2 (~CS)
DACDATA: U9.25 (GPIO19), U10.4 (SDI)
DACSCK: U9.24 (GPIO18), U10.3 (SCK)
DATA: U1.36 (DATA), U2.36 (DATA), U3.36 (DATA), U4.36 (DATA), U5.36 (DATA), U9.10 (GPIO7)
GND: C1.2, C3.2, C4.2, C5.2, C6.2, C7.2, C8.1, DC1.1, J5.1, J5.3, J8.7, J8.8, JVEE1.1, JVEE1.4, JpVDD2.3, JpVDD4.1, RV1.3, TP9.1, U1.10 (P/_S), U1.12 (VSS), U1.18 (AX1), U1.19 (AX2), U1.20 (AY0), U1.21 (AY1), U1.40 (AY2), U1.42 (AX3), U1.43 (AX0), U2.10 (P/_S), U2.12 (VSS), U2.18 (AX1), U2.19 (AX2), U2.20 (AY0), U2.21 (AY1), U2.40 (AY2), U2.42 (AX3), U2.43 (AX0), U3.10 (P/_S), U3.12 (VSS), U3.18 (AX1), U3.19 (AX2), U3.20 (AY0), U3.21 (AY1), U3.40 (AY2), U3.42 (AX3), U3.43 (AX0), U4.10 (P/_S), U4.12 (VSS), U4.18 (AX1), U4.19 (AX2), U4.20 (AY0), U4.21 (AY1), U4.40 (AY2), U4.42 (AX3), U4.43 (AX0), U5.2 (X15), U5.10 (P/_S), U5.12 (VSS), U5.18 (AX1), U5.19 (AX2), U5.20 (AY0), U5.21 (AY1), U5.40 (AY2), U5.42 (AX3), U5.43 (AX0), U9.3 (GND), U9.8 (GND), U9.13 (GND), U9.18 (GND), U9.23 (GND), U9.28 (GND), U9.33 (AGND), U9.38 (GND), U10.5 (~LDAC), U10.7 (Vss), U11.11 (V-)
JP1: J1.4, U1.33 (Y0), U2.33 (Y0), U5.33 (Y0)
JP2: J1.3, U1.35 (Y1), U2.35 (Y1), U5.35 (Y1)
JP3: J1.2, U1.37 (Y2), U2.37 (Y2), U5.37 (Y2)
JP4: J1.1, U1.39 (Y3), U2.39 (Y3), U5.39 (Y3)
JP5: J1.8, U1.17 (Y4), U2.17 (Y4), U5.24 (X13)
JP6: J1.7, U1.15 (Y5), U2.15 (Y5), U5.25 (X12)
JP7: J1.6, U1.13 (Y6), U2.13 (Y6), U5.26 (X5)
JP8: J1.5, U1.11 (Y7), U2.11 (Y7), U5.27 (X4)
JP9: J2.4, U3.33 (Y0), U4.33 (Y0), U5.8 (X11)
JP10: J2.3, U3.35 (Y1), U4.35 (Y1), U5.7 (X10)
JP11: J2.2, U3.37 (Y2), U4.37 (Y2), U5.6 (X9)
JP12: J2.1, U3.39 (Y3), U4.39 (Y3), U5.5 (X8)
JP13: J2.8, U3.17 (Y4), U4.17 (Y4), U5.17 (Y4)
JP14: J2.7, U3.15 (Y5), U4.15 (Y5), U5.15 (Y5)
JP15: J2.6, U3.13 (Y6), U4.13 (Y6), U5.13 (Y6)
JP16: J2.5, U3.11 (Y7), U4.11 (Y7), U5.11 (Y7)
unnamed: C2.2, DC1.3, JpVDD3.2, R12.1
unnamed: C2.1, DC1.4, JpVDD2.2, R12.2
unnamed: J3.17, JP3.1 (A)
unnamed: J3.34, JP1.2 (B)
unnamed: J4.17, JP4.1 (A)
unnamed: J4.34, JP2.2 (B)
unnamed: TP0.1, U9.11 (GPIO8)
unnamed: TP1.1, U9.12 (GPIO9)
unnamed: TP2.1, U9.14 (GPIO10)
unnamed: TP3.1, U9.15 (GPIO11)
unnamed: TP4.1, U9.16 (GPIO12)
unnamed: TP5.1, U9.17 (GPIO13)
unnamed: TP7.1, U9.19 (GPIO14)
unnamed: TP8.1, U9.20 (GPIO15)
unnamed: R4.1, R5.1, U11.3 (+)
unnamed: R1.2, U11.1, U11.2 (-)
unnamed: C1.1, RV1.2, TP6.1, U11.5 (+)
unnamed: R6.1, R7.1, U11.10 (+)
unnamed: R2.2, U11.8, U11.9 (-)
unnamed: R8.1, R9.1, U11.12 (+)
unnamed: R3.2, U11.13 (-), U11.14
RST: U1.41 (RST), U2.41 (RST), U3.41 (RST), U4.41 (RST), U5.41 (RST), U9.9 (GPIO6)
V3P3: JpVDD4.3, JpVDD5.3, RV1.1, U9.36 (3V3)
V165: J8.1, J8.2, J8.3, J8.4, J8.5, J8.6, U11.6 (-), U11.7
VBUS: C4.1, DC1.2, JpVDD1.1, JpVDD3.1, U9.40 (VBUS)
VCC: J6.2, J6.4, JpVDD4.2
VDD: J5.2, J5.4, JP1.1 (A), JP2.1 (A), JpVDD5.2, U5.28 (X3)
VDD1: C5.1, C7.1, JpVDD1.2, JpVDD2.1, JpVDD5.1, U1.38 (VDD), U2.38 (VDD), U3.38 (VDD), U4.38 (VDD), U5.38 (VDD)
VEE: C3.1, J6.1, J6.3, JP3.2 (B), JP4.2 (B), JVEE1.3, U5.1 (X14)
VEE1: C8.2, JVEE1.2, JpVDD3.3, U1.16 (VEE), U2.16 (VEE), U3.16 (VEE), U4.16 (VEE), U5.16 (VEE)
VSYS: C6.1, JpVDD1.3, U9.39 (VSYS), U10.1 (Vdd), U11.4 (V+)

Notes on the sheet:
Vin+
Vout+
Vout-
Vin-

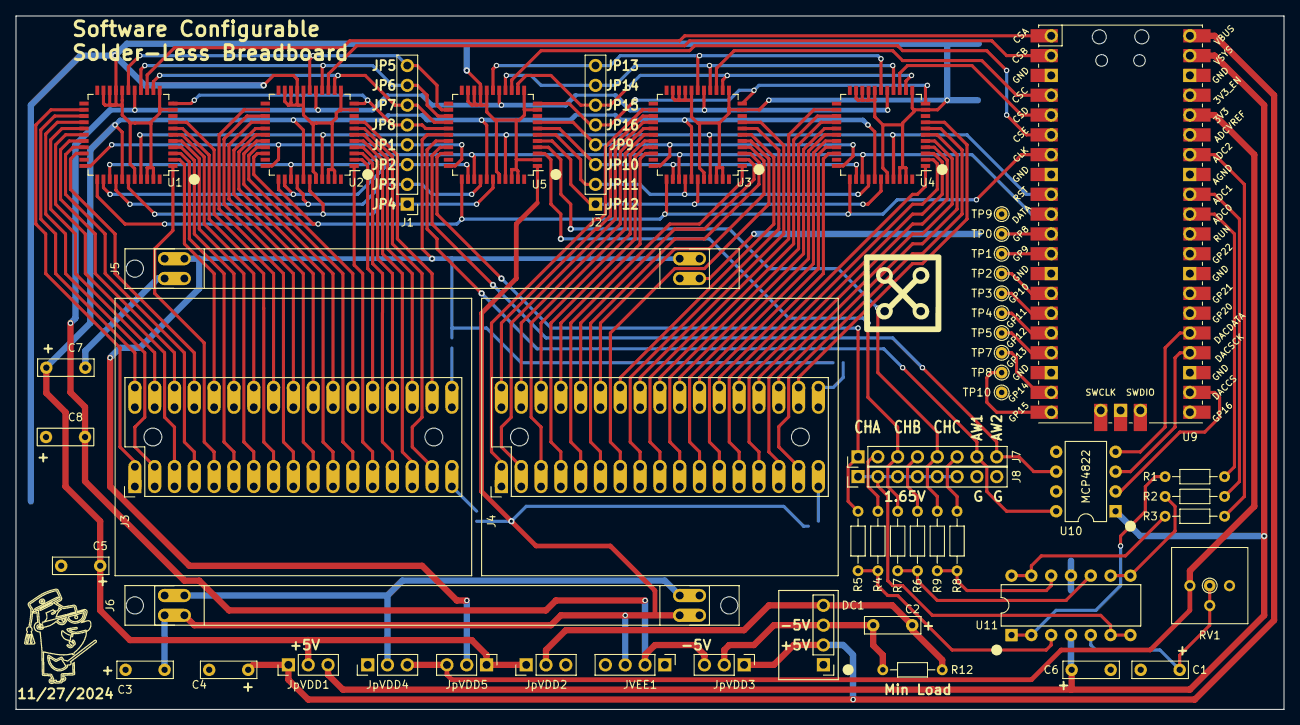
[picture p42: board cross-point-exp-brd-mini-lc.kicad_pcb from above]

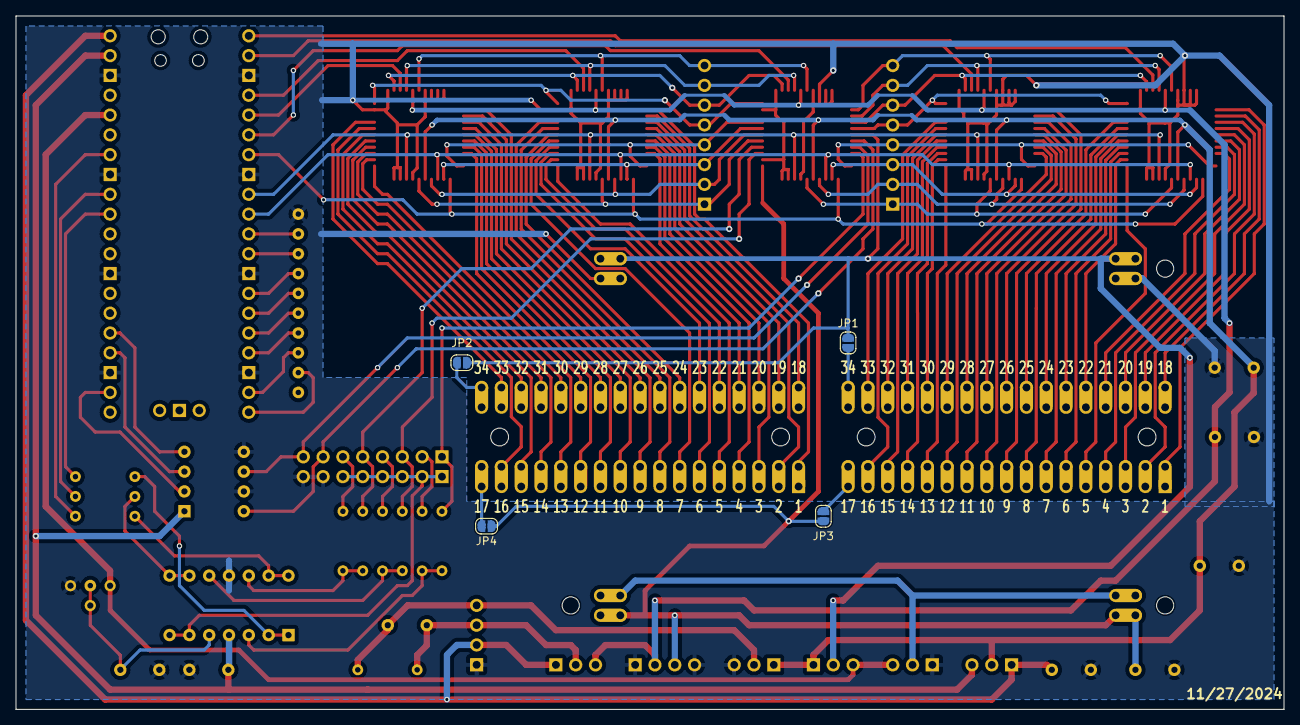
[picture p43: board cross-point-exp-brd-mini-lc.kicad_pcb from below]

Board: 2 copper layers, 162.6 x 88.9 mm, 57 parts (4 on the bottom side), 133 nets.

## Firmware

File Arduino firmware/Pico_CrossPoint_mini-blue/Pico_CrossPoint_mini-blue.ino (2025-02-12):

//Pico_CrossPoint controller using mini blue solderless breadboards with MCP4822 DAC
// 12/10/2025
#include "pico/stdlib.h"
#include "hardware/adc.h"
#include "hardware/pwm.h"
#include <hardware/timer.h>
#include <hardware/irq.h>
#include <SPI.h>
#include "pico/multicore.h"

#define ALARM_NUM 1
#define ALARM_IRQ TIMER_IRQ_1

uint8_t scopea[16384]; // 14336/8 ~ 1700 max samples
//  uint8_t digin[4096];
uint16_t awgouta[4096];
uint16_t awgoutb[4096];

short led = 25;
short awgona;
short awgonb;
short awgtpa;
short awgtpb;
short addr;
short data;
short awgdata;
short awgres;
short n;
short m;
short xadr = 0;
short yadr = 0;
short cadr = 1;
short swon = 0;
uint32_t tg;
short sync = 0;
short point = 0;
float Step;
unsigned int at, at2, st, st2, stReal;
short bmax=4096;
short amax=4096;
short bs=1024;
uint16_t tbs=2048;
uint16_t rbs=3072;
uint16_t fbs=4096;
uint16_t vbs=5120;
uint16_t sbs=6144;
uint16_t ebs=7168;
uint16_t gbs=8192;
short dy=1;
uint16_t ns=1024;
uint16_t ms=1024;
int pwmf = 500;
int pwid = 500;

static void alarm_irq(void) {
  hw_clear_bits(&timer_hw->intr, 1u << ALARM_NUM);
  alarm_in_us_arm(at);
  if (awgona == 1){ // send data to DAC A
    if (n >= ns) n = 0;
    SPI.transfer16(awgouta[n]);
    n++;
  } else {
    n = 0;
  }
  if (awgonb == 1) { // send data to DAC B
    if (m >= ms) m = 0;
    SPI.transfer16(awgoutb[m]);
    m++;
  }
  else {
    m = 0;
  }
}

static void alarm_in_us_arm(uint32_t delay_us) {
  uint64_t target = timer_hw->timerawl + delay_us;
  timer_hw->alarm[ALARM_NUM] = (uint32_t) target;
}

static void alarm_in_us(uint32_t delay_us) {
  hw_set_bits(&timer_hw->inte, 1u << ALARM_NUM);
  irq_set_exclusive_handler(ALARM_IRQ, alarm_irq);
  irq_set_enabled(ALARM_IRQ, true);
  alarm_in_us_arm(at);
}

void setup1() {
  at=20;
  awgona = 0; // default AWG A off
  awgonb = 0; // default AWG B off
  alarm_in_us(at);
}

void loop1() {
  
}
  
void setup() {
  
  Serial.begin(2000000);
  pinMode(led, OUTPUT);
  pinMode(0, OUTPUT); // CSA strobe for switch chip A 
  pinMode(1, OUTPUT); // CSB strobe for switch chip B 
  pinMode(2, OUTPUT); // CSC strobe for switch chip C
  pinMode(3, OUTPUT); // CSD strobe for switch chip D 
  pinMode(4, OUTPUT); // CSE strobe for switch chip E 
  pinMode(5, OUTPUT); // common Clock input
  pinMode(6, OUTPUT); // common Reset input
  pinMode(7, OUTPUT); // common Data input
  pinMode(8, OUTPUT); 
  pinMode(9, OUTPUT); 
  pinMode(10, OUTPUT); 
  pinMode(11, OUTPUT); 
  pinMode(12, OUTPUT); 
  pinMode(13, OUTPUT); 
  pinMode(14, OUTPUT); 
  pinMode(15, OUTPUT); 
  // preset cross point control lines
  digitalWrite(5, HIGH); // CLK input idles High
  delayMicroseconds(6); // Wait
  digitalWrite(6, HIGH); // Toggel Reset pin High
  delayMicroseconds(6); // Wait
  digitalWrite(6, LOW); // Reset input defaults Low
  digitalWrite(7, LOW); // Data input defaults Low
  digitalWrite(0, LOW); // Chip A Strobe input defaults Low
  digitalWrite(1, LOW); // Chip B Strobe input defaults Low
  digitalWrite(2, LOW); // Chip C Strobe input defaults Low
  digitalWrite(3, LOW); // Chip D Strobe input defaults Low
  digitalWrite(4, LOW); // Chip E Strobe input defaults Low

  analogWriteFreq(pwmf);
  analogWriteRange(1000);
  adc_init();
  adc_gpio_init(26); // ADC0
  adc_gpio_init(27); // ADC1
  adc_gpio_init(28); // ADC2
  adc_gpio_init(29); // ADC3
  adc_select_input(0);
  SPI.begin(true); // Start up SPI for DAC
  SPI.beginTransaction(SPISettings(25000000, MSBFIRST, SPI_MODE0));  
  //alarm_in_us(at);
} 

void loop() {
  
  int measa;
  int measb;
  int measc;
  int digmeas;
  int VDD;
  char c, c2;
  uint32_t ta, TotalReal, StartReal;
  st=11;
  awgres = 4095;
  at=20;
  short Ain1;
  Ain1 = 0; // 26; // pin number for A1
  short Ain2;
  Ain2 = 1; // 27; // pin number for A2
  short Ain3;
  Ain3 = 2; // 28; // pin number for A3
  short Ain4;
  Ain4 = 3; // 29; // pin number for A4

  while (true) { 
    if (Serial.available()){
      c=Serial.read();
      switch (c){
        case 'I': // read back FW Rev
          Serial.println ("Pi Pico Cross Point Mini Blue");
          break;
        case 'T': // change the AWG value of at in uSec both channels must be same rate
          at2 = Serial.parseInt();
          if(at2>0){
            at=at2;
          }
          break;
        case 'N': // change number of AWG A samples 
          ns = Serial.parseInt();
          if(ns>bmax){
            ns=bmax;
          }
          break;
        case 'M': // change number of AWG B samples 
          ms = Serial.parseInt();
          if(ms>bmax){
            ms=bmax;
          }
          break;
        case 'L': // load AWG A Buffer data
          addr = Serial.parseInt();
          if(addr > 2047){
              addr=2047;
            }
            if(addr < 0){
              addr=0;
            }
          c2 = Serial.read();
          if(c2=='D'){
            data = Serial.parseInt();
            if(data > awgres){
              data=awgres;
            }
            if(data < 0){
              data=0;
            }
          } else {
            data = 0;
          }
          awgouta[addr] = data | 0b0001000000000000; // address DACA 2X REF MCP4822
          break;
        case 'l': // load AWG B Buffer data
          addr = Serial.parseInt();
          if(addr > 2047){
              addr=2047;
            }
            if(addr < 0){
              addr=0;
            }
          c2 = Serial.read();
          if(c2=='D'){
            data = Serial.parseInt();
            if(data > awgres){
              data=awgres;
            }
            if(data < 0){
              data=0;
            }
          } else {
            data = 0;
          }
          awgoutb[addr] = data | 0b1001000000000000; // address DACB 2X REF MCP4822
          break;
        case 't': // change the Scope value of dt in uSec
          st2 = Serial.parseInt();
          if(st2>0){
            st=st2;
          }
          break;
        case 'b': // change number of samples to capture
          bs = Serial.parseInt();
          if(bs>bmax){
            bs=bmax;
          }
          tbs = bs * 2;
          rbs = bs * 3;
          fbs = bs * 4;
          vbs = bs * 5;
          sbs = bs * 6;
          ebs = bs * 7;
          gbs = bs * 8;
          break;
        case 'G': // enable - disable AWG A output
          c2 = Serial.read();
          if(c2=='o'){
            awgona = 1;
          }else{
            awgona = 0;
          }
          break;
        case 'g': // enable - disable AWG A output
          c2 = Serial.read();
          if(c2=='o'){
            awgonb = 1;
          }else{
            awgonb = 0;
          }
          break;
        case 'R': // Reset AWG start point at start of aquire
          sync = Serial.parseInt();
          break;
        case 'r': // Set AWG start address when case R > 0
          point = Serial.parseInt();
          break;
        case 's': // enable - disable PWM output
          c2 = Serial.read();
          if(c2=='o'){
            analogWrite (22, pwid); 
          }else{
            analogWrite (22, 0); 
          }
          break;
        case 'p': // change analog write pwm frequency value
          pwmf = Serial.parseInt();
          analogWriteFreq( pwmf );
          break;
        case 'm': // change pwm duty cycle % 
          pwid = Serial.parseInt(); // range from 0 (0%) to 1000 (100%)
          break;
        case 'V': // Read back the 3.3 V supply voltage divider 1/3
          adc_select_input(3);
          sleep_ms(1);
          VDD=adc_read();
          Serial.print ("V=");
          Serial.println ((int) VDD);
          break;
        case 'A': // set input pin value for scope channel Ain1
          Ain1 = Serial.parseInt();
          break;
        case 'B': // set input pin value for scope channel Ain2
          Ain2 = Serial.parseInt();
          break;
        case 'C': // set input pin value for scope channel Ain3
          Ain3 = Serial.parseInt();
          break;
        case 'D': // set input pin value for scope channel Ain4
          Ain4 = Serial.parseInt();
          break;
        case '1': // do scope ch a single capture
        // if sync is on reset start of awg buffer pointer
          if (sync > 0 ) {
            if (awgona == 1 || awgonb == 1){
              awgtpa = awgona;
              awgtpb = awgonb;
              awgona = 0;
              awgonb = 0;
              while ( n != point || m != point ) {
                n = point;
                m = point;
              }
              delayMicroseconds(6);
              awgona = awgtpa;
              awgonb = awgtpb;
              delayMicroseconds(sync);
            }
          }
          ta = time_us_32();
          adc_select_input(Ain1);
          StartReal = ta;
          for (int i = 0; i < bs; i++){ // Fill Buffer
            measa = adc_read(); // analogRead(A1);
            scopea[i] = (measa & 0xFF00) >> 8;
            scopea[i+bs] = measa & 0xFF;
            ta+=st;
            while (ta>time_us_32());
          }
          TotalReal=time_us_32()-StartReal;
          //stReal=TotalReal/bs; // calculate the average time for each reading
          digitalWrite(led, HIGH); // Toggel LED High while sending data
          Serial.print("stReal= ");
          Serial.println(TotalReal); // report total time for bs samples
          // dump buffer over serial
          Serial.write(scopea, tbs);
          Serial.println("");
          //
          digitalWrite(led, LOW);
          break;
          //
        case '2': // do scope ch a and b single capture
        // if sync is on reset start of awg buffer pointer
          if (sync > 0 ) {
            if (awgona == 1 || awgonb == 1){
              awgtpa = awgona;
              awgtpb = awgonb;
              awgona = 0;
              awgonb = 0;
              while ( n != point || m != point ) {
                n = point;
                m = point;
              }
              delayMicroseconds(6);
              awgona = awgtpa;
              awgonb = awgtpb;
              delayMicroseconds(sync);
            }
          }
          ta = time_us_32();
          StartReal = ta;
          for (int i = 0; i < bs; i++){ // Fill Buffer
            adc_select_input(Ain1);
            measa = adc_read();
            adc_select_input(Ain2);
            measb = adc_read();
            scopea[i] = (measa & 0xFF00) >> 8;
            scopea[i+bs] = measa & 0xFF;
            scopea[i+tbs] = (measb & 0xFF00) >> 8;
            scopea[i+rbs] = measb & 0xFF;
            ta+=st;
            while (ta>time_us_32());
          }
          TotalReal=time_us_32()-StartReal;
          //stReal=TotalReal/bs; // calculate the average time for each reading
          digitalWrite(led, HIGH); // Toggel LED High while sending data
          Serial.print("stReal= ");
          Serial.println(TotalReal);
          // Dump Buffer over serial
          Serial.write(scopea, fbs);
          Serial.println("");
          //
          digitalWrite(led, LOW);  // turn the LED off (HIGH is the voltage level)
          break;
          //
        case '3': // do scope ch a b and c single capture
        // if sync is on reset start of awg buffer pointer
          if (sync > 0 ) {
            if (awgona == 1 || awgonb == 1){
              awgtpa = awgona;
              awgtpb = awgonb;
              awgona = 0;
              awgonb = 0;
              while ( n != point || m != point ) {
                n = point;
                m = point;
              }
              delayMicroseconds(6);
              awgona = awgtpa;
              awgonb = awgtpb;
              delayMicroseconds(sync);
            }
          }
          ta = time_us_32();
          StartReal = ta;
          for (int i = 0; i < bs; i++){ // Fill Buffer
            adc_select_input(Ain1);
            measa = adc_read();
            adc_select_input(Ain2);
            measb = adc_read();
            adc_select_input(Ain3);
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

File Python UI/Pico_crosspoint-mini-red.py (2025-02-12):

#
# Hardware specific interface functions
# For pi pico Cross Point Exp Board Mini Red
# Three analog + 2 AWG channel scope
# Mini breadboard Ver 1
# (2-6-2025)
# Written using Python version 3.10, Windows OS 
#
try:
    import serial
    import serial.tools.list_ports
except:
    root.update()
    showwarning("WARNING","Serial Library not installed?!")
    root.destroy()
    exit()
#
# adjust for your specific hardware by changing these values in the alice.init file
ADC_Cal = 3.29
AWGPeakToPeak = 4.095 # Iternal reference voltage for MCP4822
#
AWGRes = 4095 # For 8 bits, 4095 for 12 bits, 1023 for 10 bits
ConfigFileName = "alice-last-config.cfg"
CHANNELS = 3 # Number of supported Analog input channels
AWGChannels = 2 # Number of supported Analog output channels
PWMChannels = 1 # Number of supported PWM output channels
DigChannels = 0 # Number of supported Dig channels
LogicChannels = 0 # Number of supported Logic Analyzer channels
EnablePGAGain = 0 #
EnableAWGNoise = 0 #
UseSoftwareTrigger = 1
AllowFlashFirmware = 1
Tdiv.set(10)
MatrixStatus = IntVar()
MatrixStatus.set(0)
AWG_Amp_Mode.set(0)
DevID = "Pi Pico Cross Point Mini"
SerComPort = 'Auto'
TimeSpan = 0.01
InterpRate = 4
EnableInterpFilter.set(1)
MaxSampleRate = SAMPLErate = 333333*InterpRate
ATmin = 8 # set minimum DAC update rate to 8 uSec
MaxAWGSampleRate = 1.0 / (ATmin / 1000000) # set to 1 / 8 uSec
AWGSampleRate = MaxAWGSampleRate
LSBsizeA =  LSBsizeB = LSBsizeC = LSBsize = ADC_Cal/4096.0
HardwareBuffer = 2048 # Max hardware waveform buffer size
MinSamples = 2048 # capture sample buffer size
AWGBuffLen = 2048 # Max DAC hardware waveform buffer size
Cycles = 1
SMPfft = MinSamples*InterpRate # Set FFT size based on fixed acquisition record length
#
VBuffA = numpy.ones(MinSamples*InterpRate)
VBuffB = numpy.ones(MinSamples*InterpRate)
VBuffC = numpy.ones(MinSamples*InterpRate)
VBuffD = numpy.ones(MinSamples*InterpRate)
VBuffG = numpy.ones(MinSamples*InterpRate)
MBuff = numpy.ones(MinSamples*InterpRate)
MBuffX = numpy.ones(MinSamples*InterpRate)
MBuffY = numpy.ones(MinSamples*InterpRate)
VmemoryA = numpy.ones(MinSamples*InterpRate) # The memory for averaging
VmemoryB = numpy.ones(MinSamples*InterpRate) # The memory for averaging
VmemoryC = numpy.ones(MinSamples*InterpRate)
VmemoryD = numpy.ones(MinSamples*InterpRate)
#
IACMString = "+2.5"
IA_Mode.set(1)
#
# Breadboard pin maping for Mimi Red 1 layout
#
TL1 = "CA0"; TL2 = "CA1"; TL3 = "CA2"; TL4 = "CA3"; TL5 = "CA4"; TL6 = "CA5"; TL7 = "CA12"; TL8 = "CA13"
BL1 = "CA14"; BL2 = "CA15"; BL3 = "CA6"; BL4 = "CA7"; BL5 = "CA8"; BL6 = "CA9"; BL7 = "CA10"; BL8 = "CA11"
TL9 = "CB0"; TL10 = "CB1"; TL11 = "CB2"; TL12 = "CB3"; TL13 = "CB4"; TL14 = "CB5"; TL15 = "CB12"; TL16 = "CB13"
BL9 = "CB14"; BL10 = "CB15"; BL11 = "CB6"; BL12 = "CB7"; BL13 = "CB8"; BL14 = "CB9"; BL15 = "CB10"; BL16 = "CB11"
TL17 = "CE0"; TR1 = "CE2"
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

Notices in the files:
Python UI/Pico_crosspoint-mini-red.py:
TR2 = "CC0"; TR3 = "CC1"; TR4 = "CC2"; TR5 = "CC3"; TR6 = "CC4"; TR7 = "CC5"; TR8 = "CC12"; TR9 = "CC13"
